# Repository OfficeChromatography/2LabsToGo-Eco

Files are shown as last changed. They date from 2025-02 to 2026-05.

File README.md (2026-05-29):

# 2LabsToGo-Eco

# Important Preliminary Note
<b>In our publication (reference 1) we recommended asking our electronic workshop for a quote on the electronic boards. Unfortunately, that turned out to be very difficult. We therefore recommend contacting Chromnil (https://chromnil.com/), a young start-up also providing the electronic boards or even the 2LabsToGo-Eco ready mounted.<br>
<br>

## 2LabsToGo-Eco combines an analytical (high-performance thin-layer chromatography) and a biological (bioassays) laboratory.

### References:  
<ol>
<li>M.C.O. Romero, K. Jakob, J. Schmidt, T. Nimmerfroh, W. Schwack, G.E.
 Morlock, Consolidating two laboratories into the most sustainable lab of the future: 2LabsToGo-Eco,  Analytica Chimica Acta (2025) 1367, 344103 (https://doi.org/10.1016/j.aca.2025.344103).</li>
<li>A. Haase, W. Schwack, G. Morlock, Humidity control for the 2LabsToGo-Eco, 
Analytica Chimica Acta (2026) 1382, 344811 (https://doi.org/10.1016/j.aca.2025.344811).</li>
<li>W. Schwack, J. Morlock, L. Sing, G. Morlock, Faster Operation of 2LabsToGo-Eco 
 Using Debian 13, Django 5, and Raspberry Pi 5, verified via screening of cannabidiol-containing oils,
 Journal of Planar Chromatography (2026) 39:119–124, (https://doi.org/10.1007/s00764-026-00406-x).</(li>
</ol>
This repository contains the folders for the hardware, firmware, and software for 2LabsToGo-Eco.
For details and instructions consult the given references.

### 1. Raspberry Pi operating system (OS)
The recent Raspberry Pi OS is based on Debain 13 (Trixie, https://www.raspberrypi.com/software/operating-systems/) 
that can be used to install 2LabsToGo-Eco on both the Raspberry Pi 4B and 
the Raspberry Pi 5B (see reference 3).

### 2. Clone the 2LabsToGo-Eco repository
The simplest way to clone a git repository (internet access required!) is opening a new terminal being in the home directory.<br>
Then, copy and paste the next command and press enter.
```bash
git clone https://github.com/OfficeChromatography/2LabsToGo-Eco.git
```
### 3. Installing the software
To install the software, consult this [README](https://github.com/OfficeChromatography/2LabsToGo-Eco/blob/main/2LabsToGo-Eco-Software/README.md).

### 4. Flashing the firmware
Instructions to flash the firmware, can be found [here](https://github.com/OfficeChromatography/2LabsToGo-Eco/blob/main/2LabsToGo-Eco-Firmware/README.md).

### 5. Updating 2LabsToGo-Eco
Instructions to update the 2LabsToGo-Eco folder, consult [this instruction folder](https://github.com/OfficeChromatography/2LabsToGo-Eco/tree/main/2LabsToGo-Update-History).

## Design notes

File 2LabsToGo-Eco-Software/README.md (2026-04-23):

# 2LabsToGo-Eco-Software
## Installation
The installation process is really simple. 

2LabsToGo-Eco-Software works fine on a Raspberry Pi 4B or 5B with 4GB RAM memory.

As operation system, Raspberry Pi OS (Debian 13, trixie, 64-bit) is recommended,
installed by the [Raspberry Pi Imager](https://www.raspberrypi.com/software/) (see reference 3 in 
this [README](https://github.com/OfficeChromatography/2LabsToGo-Eco/blob/main/README.md)).

Before the next steps, consult the [checklist](https://github.com/OfficeChromatography/2LabsToGo-Eco/blob/main/2LabsToGo-Update-History/checklist.pdf) and  [Update Assembly Instruction](https://github.com/OfficeChromatography/2LabsToGo-Eco/blob/main/2LabsToGo-Update-History/UpdateAssemblyInstruction.pdf).

To clone the 2LabsToGo-Eco repository, consult this [README](https://github.com/OfficeChromatography/2LabsToGo-Eco/blob/main/README.md).

### Execute 'install.py'
To install 2LabsToGo-Eco-Software, go to the folder that contains the 2LabsToGo-Eco-Software with

```bash
cd /path/to/your/2LabsToGo-Eco-Software
```
Then execute
```bash
sudo python3 install.py |& tee install-py.log
```

This will install:
```
docker and some software packages
```
After some minutes, 2LabsToGo-Eco-Software is installed in your device.

To start the server execute the run.py file with
```
sudo python3 run.py |& tee run-py.log
```
This process takes a while, when executed the first time. The log files can be consulted in case of any problem.<a>

To quit the Django server, press
```
Ctrl+c 
```

2LabsToGo-Eco-Software was intensively tested with both Chromium and Firefox as browser.

To use the software consult the 2LabsToGo-Eco-Software Manual (see reference 1 in 
this [README](https://github.com/OfficeChromatography/2LabsToGo-Eco/blob/main/README.md)).

### Useful guides

[Docker Commands](https://towardsdatascience.com/15-docker-commands-you-should-know-970ea5203421)

[Remove Migrations](https://simpleisbetterthancomplex.com/tutorial/2016/07/26/how-to-reset-migrations.html)

All commands must be executed inside the docker-compose. To enter to the docker-compose running instance:

In a running container:
```sh
sudo docker-compose exec -ti app bash
```
To initialize and enter the terminal
```sh
sudo docker-compose run -ti app bash
```

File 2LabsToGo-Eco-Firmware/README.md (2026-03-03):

# 2LabsToGo-Eco Firmware 
A Marlin 2.0 3D Printer based Firmware

## Marlin 2.0

Marlin 2.0 takes this popular RepRap firmware to the next level by adding support for much faster 32-bit and ARM-based boards while improving support for 8-bit AVR boards. Read about Marlin's decision to use a "Hardware Abstraction Layer" below.

## Building 2LabsToGo-Eco Firmware

To build the firmware, [PlatformIO](http://docs.platformio.org/en/latest/ide.html#platformio-ide) is preferred. 
Detailed instructions are also available in [Instruction Visual Studio Code](https://github.com/OfficeChromatography/2LabsToGo-Eco/blob/main/2LabsToGo-Eco-Firmware/Instruction%20Visual%20Studio%20Code.pdf).

For building the firmware open the folder 2LabsToGo-Eco-Marlin in Visual Studio Code.
The built firmware.hex file is then saved in 2LabsToGo-Eco-Firmware/2LabsToGo-Eco-Marlin/.pio/build/mega2560.

<b>However, building the firmware is only required, if the Marlin codes have been modified.</b><a>

A pre-built firmware file (firmware_2LabsToGo-Eco.hex) is available in this folder, including files for setting the fuses and flashing the bootloader.
To flash the firmware from the Raspberry Pi onto the Arduino chip of the 2LabsToGo-Eco mainboard, 
use the bash script <u>2LabsToGo-Eco-Firmware/Bullseye/flash_firmware_bullseye.sh</u> or 
<u>2LabsToGo-Eco-Firmware/Trixie/flash_firmware_trixie.sh</u>, depending upon the used Raspberry Pi OS.

For more details on flashing, consult the [2LabsToGo-Eco Assembly guide](https://doi.org/10.1016/j.aca.2025.344103) and reference 3 in this [README](https://github.com/OfficeChromatography/2LabsToGo-Eco/blob/main/README.md).
 
## After firmware update
After a firmware update, both PID tunings must be performed again to save the settings in the firmware.<br>
Consult the [2LabsToGo-Eco Assembly guide](https://doi.org/10.1016/j.aca.2025.344103).

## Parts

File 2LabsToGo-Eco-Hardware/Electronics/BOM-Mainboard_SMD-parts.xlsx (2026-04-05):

 | SMD parts
ID | Designator | Qty. | Manufacturer | Manufacturer Part # | Description | Type | Footprint
1 | C2,C3,C6,C15,C37,C38,C39,C54,C63,C64,C65,C66,C67 | 13 | Panasonic | EEE-FK1E101XP | Aluminium Electrolytic Capacitors - SMD 100uF 25V | SMD | PANASONIC_D_334
2 | C9,C11,C12,C13,C14,C16,C17,C18,C19,C23,C24,C25,C26,C29,C31,C32,C35,C36,C4,C41,C42,C43,C44,C45,C47,C49,C53,C55,C56,C60,C61,C62,C68 | 33 | KEMET | C0805C104K5RACTU | Multilayer Ceramic Capacitors MLCC - SMD/SMT 50V 0.1uF X7R 0805 10% | SMD | C0805
3 | C20,C21 | 2 | KEMET | C0805C220K5RACTU | Multilayer Ceramic Capacitors MLCC - SMD/SMT 50V 22pF X7R 0805 10% | SMD | C0805_334
4 | C28,C33 | 2 | KEMET | C0805C681K5RACTU | Multilayer Ceramic Capacitors MLCC - SMD/SMT 50V 680pF X7R 0805 10% | SMD | C0805_334
5 | C30,C46 | 2 | KEMET | C0805C223K5RACTU | Multilayer Ceramic Capacitors MLCC - SMD/SMT 50V 0.022uF X7R 0805 10% | SMD | C0805_334
6 | C1,C5,C7,C8,C10,C27,C34,C51 | 8 | Panasonic | EEE-FK1E100AR | Aluminium Electrolytic Capacitors - SMD 10UF 25V FK SMD | SMD | PANASONIC_B_334
7 | C22,C48 | 2 | KEMET | C0805C101F3HACTU | Multilayer Ceramic Capacitors MLCC - SMD/SMT 25V 100pF X8R 0805 1% | SMD | C0805_334
8 | C50 | 1 | KEMET | C1812C102KHRACTU | Multilayer Ceramic Capacitors MLCC - SMD/SMT 3kV 1000pF X7R 1812 10% | SMD | C1812_334
9 | C52 | 1 | KEMET | C1812C334KCRACTU | Multilayer Ceramic Capacitors MLCC - SMD/SMT 500V 0.33uF X7R 1812 10% | SMD | C1812_334
10 | C59 | 1 | KEMET | C0805C473K5RACTU | Multilayer Ceramic Capacitors MLCC - SMD/SMT 50V 0.047uF X7R 0805 10% | SMD | C0805
11 | D4,D6,D12,D13,D14,D15 | 6 | onsemi | RGF1G | Rectifiers 400V 1a Rectifier Glass Passivated | SMD | DO214AC_210
12 | D7,D16 | 2 | onsemi | 1N4148WS | Small Signal Switching Diodes Small Signal Diode | SMD | SOD-323_11396254
13 | D1,D2,D10 | 3 | Comchip Technology | SS54-HF | Schottky Diodes & Rectifiers DIODE SCHOTTKY 5A 40V SMA | SMD | DO214AC
14 | D8,D9 | 2 | Vishay | SML4757A-E3/61 | Zener Diodes 51 Volt 1.0W 5% | SMD | DO-214AC-2
15 | IC10 | 1 | Microchip Technology | MIC4420ZM-TR | Gate Drivers 8 SOIC 3.90mm(.150in) T/R | SMD | SOIC-8
16 | IC11,IC12 | 2 | onsemi | LM1117MPX-ADJNOPB | LDO Voltage Regulators LM ANA SOT223 800MA LDO | SMD | SOT-223-3
17 | IC2,IC7 | 2 | Nexperia | 74HC4053D,653 | Multiplexer Switch ICs Triple 2-channel analog multiplexer/demultiplexer | SMD | SOIC-16
18 | IC1,IC4 | 2 | Texas Instruments | NE555DR | Timers & Support Products Precision A 595-NE555D | SMD | SOIC-8
19 | IC3,IC5,IC6 | 3 | Texas Instruments | LM358MX/NOPB | Operational Amplifiers - Op Amps LOW PWR DUAL OP AMP A 926-LM358M/NOPB | SMD | SOIC-8
20 | IC8 | 1 | Texas Instruments | SE555DRG4 | Timers & Support Products Prec Timer ALT 595-SE555DR | SMD | SOIC-8
21 | IC9 | 1 | Diodes Incorporated | AS7805ADTR-G1 | Linear Voltage Regulators 1A 3-Term POS Reg Output 1A | SMD | TO-252-2
22 | Q1,Q2,Q3,Q6,Q7,Q8,Q9 | 7 | Infineon Technologies | IRFR3410TRPBF | MOSFETs 100V SINGLE N-CH 39mOhms 37nC | SMD | TO-252-3
23 | Q5 | 1 | Infineon Technologies | IPD60R180P7SAUMA1 | MOSFETs CONSUMER | SMD | TO-252-3
24 | R10,R9,R56,R55,R6,R2,R26,R5,R8,R54,R100,R4,R82 | 13 | YAGEO | RC0805FR-07100KL | Thick Film Resistors - SMD 100 kOhms 125 mW 0805 1% | SMD | R0805_334
25 | R103,R12 | 2 | YAGEO | RC0805FR-13120RL | Thick Film Resistors - SMD 120Ohms 1/8W 0805 1% | SMD | R0805_334
26 | R13,R14,R15,R31,R47,R53,R87,R99,R106 | 9 | YAGEO | RC0805FR-0710RL | Thick Film Resistors - SMD 10 Ohms 125 mW 0805 1% | SMD | R0805_334
27 | R23,R24,R25,R35,R38,R40,R57,R61,R63,R68,R71,R73,R90,R95,R96,R97 | 16 | YAGEO | RC0805FR-071KL | Thick Film Resistors - SMD 1 kOhms 125 mW 0805 1% | SMD | R0805_334
28 | R16,R18,R19,R20,R27,R29,R32,R36,R43,R45,R48,R58,R65,R69,R76,R78,R79 | 17 | YAGEO | RC0805FR-0710KL | Thick Film Resistors - SMD 10 kOhms 125 mW 0805 1% | SMD | R0805_334
29 | R3,R39,R62,R72 | 4 | YAGEO | RC0805FR-071ML | Thick Film Resistors - SMD 1 MOhms 125 mW 0805 1% | SMD | R0805_334
30 | R66,R67,R77 | 3 | YAGEO | RL1206FR-070R1L | Current Sense Resistors - SMD 100 mOhms 250mW 1 % 600 ppm/C | SMD | R1206_334
31 | R1,R7,R11,R21,R22,R33,R37,R49,R59,R70,R102 | 11 | YAGEO | RC0805FR-074K7L | Thick Film Resistors - SMD 4.7 kOhms 125 mW 0805 1% | SMD | R0805_334
32 | R83 | 1 | YAGEO | RC0805FR-07100RL | Thick Film Resistors - SMD 100 Ohms 125 mW 0805 1% | SMD | R0805_334
33 | R84 | 1 | YAGEO | RC0805JR-7W15KL | Thick Film Resistors - SMD 15kOhms 1/8W 0805 5% | SMD | R0805_334
34 | R89 | 1 | YAGEO | RC0805FR-073KL | Thick Film Resistors - SMD 3 kOhms 125 mW 0805 1% | SMD | R0805_334
35 | R91 | 1 | YAGEO | RC0805FR-0718K2L | Thick Film Resistors - SMD 18.2 kOhms 125 mW 0805 1% | SMD | R0805_334
36 | R94,R92,R30,R98,R28,R46,R101,R93,R44 | 9 | YAGEO | RC0805FR-07330RL | Thick Film Resistors - SMD 330 Ohms 125 mW 0805 1% | SMD | R0805_334
37 | T3,T1,T2,T4 | 4 | Nexperia | BC847C,215 | Bipolar Transistors - BJT 45 V, 100 mA NPN general-purpose transistors | SMD | SOT23_3
38 | T5,T6 | 2 | onsemi | MJD128T4G | Darlington Transistors BIP PNP 8A 120V TR | SMD | TO-252-3
39 | T7,T8,T9 | 3 | onsemi | MJD200G | Bipolar Transistors - BJT 5A 25V 12.5W NPN | SMD | TO-252-3
40 | U$2 | 1 | Texas Instruments | LM2577SX-ADJ/NOPB | IC REG BST FLYBACK ADJ 3A TO263 | SMD | TO-263-5
41 | U2 | 1 | Microchip Technology | ATMEGA2560-16AU | AVR AVR® ATmega Mikrocontroller IC 8-Bit 16MHz 256KB (128K x 16) FLASH 100-TQFP (14x14) | SMD | TQFP-100
42 | U4 | 1 | Texas Instruments | TXB0108PWR | Translation - Voltage Levels 8-Bit Bi-directional V-Level Translator A 595-TXB0108PWRG4 | SMD | TSSOP-20
43 | L1 | 1 | Würth Elektronik | 74477020 | FIXED IND 100UH 2.2A 220 MOHM | SMD
44 | L2 | 1 | Würth Elektronik | 744770222 | FIXED IND 220UH 1.3A 390 MOHM | SMD

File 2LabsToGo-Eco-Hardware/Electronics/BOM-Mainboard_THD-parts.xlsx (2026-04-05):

 | Through hole parts (THD)
ID | Designator | Qty. | Manufacturer | Manufacturer Part # | Description | Type | Footprint
1 | C40, C57, C58 | 3 | Panasonic Electronic Components | EEU-FR1V471L | CAP ALUM 470UF 20% 35V RADIAL TH | THD
2 | J4 | 1 | Kycon Inc. | KPJX-4S-S | CONN JACK FMALE 4POS TIN SOLDER | THD
3 | J5 | 2 | Same Sky (Formerly CUI Devices) | PJ-082BH | CONN PWR JACK 2.5X5.5MM SOLDER | THD
4 | J6 | 1 | 3M | Y2540-6002-SH 40P ST HDR 0.112 GF | 3M FOUR-WALL HEADER 2500 SERIES | THD
5 | Q4 | 1 | Abracon LLC | ABL-16.000MHZ-B2 | CRYSTAL 16.0000MHZ 18PF TH | THD
6 | R105 | 1 | Bourns Inc. | 3296W-1-102LF | TRIMMER 1K OHM 0.5W PC PIN TOP | THD
7 | R34, R50 | 2 | Bourns Inc. | 3296W-1-504LF | TRIMMER 500K OHM 0.5W PC PIN TOP | THD
8 | R41, R64, R74 | 3 | Bourns Inc. | 3296W-1-204LF | TRIMMER 200K OHM 0.5W PC PIN TOP | THD
9 | R81 | 1 | Bourns Inc. | 3296W-1-501LF | TRIMMER 500 OHM 0.5W PC PIN TOP | THD
10 | SV1 | 1 | 3M | Y2514-6002-SH 14P ST HDR 0.112 GF | 3M FOUR-WALL HEADER 2500 SERIES | THD
11 | U$1, U$4, U$6, U$7, U$8 | 20 | Amphenol CS (FCI) | 75915-308GLF | CONN RCPT 8POS 0.1 GOLD PCB | THD
12 | X1, X2, X6, X7, X11 | 5 | Phoenix Contact | 1803426 | TERM BLOCK HDR 2POS 3.81MM | THD
13 | X4 | 2 | Phoenix Contact | 1803455 | TERM BLOCK HDR 5POS 3.81MM | THD
14 | X5 | 1 | Phoenix Contact | 1803471 | TERM BLOCK HDR 7POS 3.81MM | THD
15 | X9 | 1 | Amphenol CS (FCI) | 87520-0010BLF | CONN RCPT USB2.0 TYPEA 4POS R/A | THD
16 | I2C_1, I2C_2, I2C_3, Z-MOT1, Z-MOT2, X-MOT, Y-MOT, E0-MOT, Z-STOP1, Z-STOP2, X-, X+, Y-, Y+, Z+, FAN1 | 3 | Amphenol CS (FCI) | 68002-420HLF | CONN HEADER VERT 20POS 2.54MM 1) | THD
17 | JP3 | 1 | Amphenol CS (FCI) | 67996-408HLF | CONN HEADER VERT 8POS 2.54MM | THD
18 | ISP1, JP1, JP2, JP4, JP5, JP6 | 6 | Amphenol CS (FCI) | 67996-406HLF | CONN HEADER VERT 6POS 2.54MM | THD
19 | SV3 | 1 | Amphenol CS (FCI) | 67996-410HLF | CONN HEADER VERT 10POS 2.54MM | THD
20 | SV4 | 1 | Amphenol CS (FCI) | 67996-420HLF | CONN HEADER VERT 20POS 2.54MM | THD
21 | SV5 | 1 | Amphenol CS (FCI) | 67996-412HLF | CONN HEADER VERT 12POS 2.54MM | THD
22 | X8 | 1 | Phoenix Contact | 1876301 | TERM BLOCK HDR 6POS 3.50MM | THD
23 | SW1 | 1 | TE Connectivity ALCOSWITCH Switches | 1825910-6 | SWITCH TACTILE SPST-NO 0.05A 24V | THD
24 | R88 | 1 | Bourns Inc. | 3296W-1-104ALF | TRIMMER 100K OHM 0.5W PC PIN TOP | THD
25 | J2 | 1 | Mean Well USA Inc. | NID65-5 | DC DC CONVERTER 5V 33W | THD
26 | X10 | 1 | Phoenix Contact | 1755752 | TERM BLOCK HDR 4POS 5.08MM | THD
27 | DHT1 | 1 | Molex | 901471104 | CONN RCPT 4POS 0.1 TIN PCB | THD
 | 1) Header to be cut to 2-pin (FAN1), 3-pin (Z-STOP1, Z-STOP2, X-, X+, Y-, Y+, Z+) and 4-pin (I2C_1, I2C_2, I2C_3, Z-MOT1, Z-MOT2, X-MOT, Y-MOT, E0-MOT) parts, respectively

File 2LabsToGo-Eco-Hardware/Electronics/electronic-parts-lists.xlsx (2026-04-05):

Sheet: mainboard
 | SMD parts
ID | Designator | Manufacturer No | Manufacturer | Description | Termination Style | Footprint | Qty.
1 | C2,C3,C6,C15,C37,C38,C39,C54,C63,C64,C65,C66,C67 | EEE-FK1E101XP | Panasonic | Aluminium Electrolytic Capacitors - SMD 100uF 25V | SMD | PANASONIC_D_334 | 13
2 | C9,C11,C12,C13,C14,C16,C17,C18,C19,C23,C24,C25,C26,C29,C31,C32,C35,C36,C4,C41,C42,C43,C44,C45,C47,C49,C53,C55,C56,C60,C61,C62,C68 | C0805C104K5RACTU | KEMET | Multilayer Ceramic Capacitors MLCC - SMD/SMT 50V 0.1uF X7R 0805 10% | SMD | C0805 | 33
3 | C20,C21 | C0805C220K5RACTU | KEMET | Multilayer Ceramic Capacitors MLCC - SMD/SMT 50V 22pF X7R 0805 10% | SMD | C0805_334 | 2
4 | C28,C33 | C0805C681K5RACTU | KEMET | Multilayer Ceramic Capacitors MLCC - SMD/SMT 50V 680pF X7R 0805 10% | SMD | C0805_334 | 2
5 | C30,C46 | C0805C223K5RACTU | KEMET | Multilayer Ceramic Capacitors MLCC - SMD/SMT 50V 0.022uF X7R 0805 10% | SMD | C0805_334 | 2
6 | C1,C5,C7,C8,C10,C27,C34,C51 | EEE-FK1E100AR | Panasonic | Aluminium Electrolytic Capacitors - SMD 10UF 25V FK SMD | SMD | PANASONIC_B_334 | 8
7 | C22,C48 | C0805C101F3HACTU | KEMET | Multilayer Ceramic Capacitors MLCC - SMD/SMT 25V 100pF X8R 0805 1% | SMD | C0805_334 | 2
8 | C50 | C1812C102KHRACTU | KEMET | Multilayer Ceramic Capacitors MLCC - SMD/SMT 3kV 1000pF X7R 1812 10% | SMD | C1812_334 | 1
9 | C52 | C1812C334KCRACTU | KEMET | Multilayer Ceramic Capacitors MLCC - SMD/SMT 500V 0.33uF X7R 1812 10% | SMD | C1812_334 | 1
10 | C59 | C0805C473K5RACTU | KEMET | Multilayer Ceramic Capacitors MLCC - SMD/SMT 50V 0.047uF X7R 0805 10% | SMD | C0805 | 1
11 | D4,D6,D12,D13,D14,D15 | RGF1G | onsemi | Rectifiers 400V 1a Rectifier Glass Passivated | SMD | DO214AC_210 | 6
12 | D7,D16 | 1N4148WS | onsemi | Small Signal Switching Diodes Small Signal Diode | SMD | SOD-323_11396254 | 2
13 | D1,D2,D10 | SS54-HF | Comchip Technology | Schottky Diodes & Rectifiers DIODE SCHOTTKY 5A 40V SMA | SMD | DO214AC | 3
14 | D8,D9 | SML4757A-E3/61 | Vishay | Zener Diodes 51 Volt 1.0W 5% | SMD | DO-214AC-2 | 2
15 | IC10 | MIC4420ZM-TR | Microchip Technology | Gate Drivers 8 SOIC 3.90mm(.150in) T/R | SMD | SOIC-8 | 1
16 | IC11,IC12 | LM1117MPX-ADJNOPB | onsemi | LDO Voltage Regulators LM ANA SOT223 800MA LDO | SMD | SOT-223-3 | 2
17 | IC2,IC7 | 74HC4053D,653 | Nexperia | Multiplexer Switch ICs Triple 2-channel analog multiplexer/demultiplexer | SMD | SOIC-16 | 2
18 | IC1,IC4 | NE555DR | Texas Instruments | Timers & Support Products Precision A 595-NE555D | SMD | SOIC-8 | 2
19 | IC3,IC5,IC6 | LM358MX/NOPB | Texas Instruments | Operational Amplifiers - Op Amps LOW PWR DUAL OP AMP A 926-LM358M/NOPB | SMD | SOIC-8 | 3
20 | IC8 | SE555DRG4 | Texas Instruments | Timers & Support Products Prec Timer ALT 595-SE555DR | SMD | SOIC-8 | 1
21 | IC9 | AS7805ADTR-G1 | Diodes Incorporated | Linear Voltage Regulators 1A 3-Term POS Reg Output 1A | SMD | TO-252-2 | 1
22 | Q1,Q2,Q3,Q6,Q7,Q8,Q9 | IRFR3410TRPBF | Infineon Technologies | MOSFETs 100V SINGLE N-CH 39mOhms 37nC | SMD | TO-252-3 | 7
23 | Q5 | IPD60R180P7SAUMA1 | Infineon Technologies | MOSFETs CONSUMER | SMD | TO-252-3 | 1
24 | R10,R9,R56,R55,R6,R2,R26,R5,R8,R54,R100,R4,R82 | RC0805FR-07100KL | YAGEO | Thick Film Resistors - SMD 100 kOhms 125 mW 0805 1% | SMD | R0805_334 | 13
25 | R103,R12 | RC0805FR-13120RL | YAGEO | Thick Film Resistors - SMD 120Ohms 1/8W 0805 1% | SMD | R0805_334 | 2
26 | R13,R14,R15,R31,R47,R53,R87,R99,R106 | RC0805FR-0710RL | YAGEO | Thick Film Resistors - SMD 10 Ohms 125 mW 0805 1% | SMD | R0805_334 | 9
27 | R23,R24,R25,R35,R38,R40,R57,R61,R63,R68,R71,R73,R90,R95,R96,R97 | RC0805FR-071KL | YAGEO | Thick Film Resistors - SMD 1 kOhms 125 mW 0805 1% | SMD | R0805_334 | 16
28 | R16,R18,R19,R20,R27,R29,R32,R36,R43,R45,R48,R58,R65,R69,R76,R78,R79 | RC0805FR-0710KL | YAGEO | Thick Film Resistors - SMD 10 kOhms 125 mW 0805 1% | SMD | R0805_334 | 17
29 | R3,R39,R62,R72 | RC0805FR-071ML | YAGEO | Thick Film Resistors - SMD 1 MOhms 125 mW 0805 1% | SMD | R0805_334 | 4
30 | R66,R67,R77 | RL1206FR-070R1L | YAGEO | Current Sense Resistors - SMD 100 mOhms 250mW 1 % 600 ppm/C | SMD | R1206_334 | 3
31 | R1,R7,R11,R21,R22,R33,R37,R49,R59,R70,R102 | RC0805FR-074K7L | YAGEO | Thick Film Resistors - SMD 4.7 kOhms 125 mW 0805 1% | SMD | R0805_334 | 11
32 | R83 | RC0805FR-07100RL | YAGEO | Thick Film Resistors - SMD 100 Ohms 125 mW 0805 1% | SMD | R0805_334 | 1
33 | R84 | RC0805JR-7W15KL | YAGEO | Thick Film Resistors - SMD 15kOhms 1/8W 0805 5% | SMD | R0805_334 | 1
34 | R89 | RC0805FR-073KL | YAGEO | Thick Film Resistors - SMD 3 kOhms 125 mW 0805 1% | SMD | R0805_334 | 1
35 | R91 | RC0805FR-0718K2L | YAGEO | Thick Film Resistors - SMD 18.2 kOhms 125 mW 0805 1% | SMD | R0805_334 | 1
36 | R94,R92,R30,R98,R28,R46,R101,R93,R44 | RC0805FR-07330RL | YAGEO | Thick Film Resistors - SMD 330 Ohms 125 mW 0805 1% | SMD | R0805_334 | 9
37 | T3,T1,T2,T4 | BC847C,215 | Nexperia | Bipolar Transistors - BJT 45 V, 100 mA NPN general-purpose transistors | SMD | SOT23_3 | 4
38 | T5,T6 | MJD128T4G | onsemi | Darlington Transistors BIP PNP 8A 120V TR | SMD | TO-252-3 | 2
39 | T7,T8,T9 | MJD200G | onsemi | Bipolar Transistors - BJT 5A 25V 12.5W NPN | SMD | TO-252-3 | 3
40 | U$2 | LM2577SX-ADJ/NOPB | Texas Instruments | Switching Voltage Regulators Step-Up Vtg Reg A 926-LM2577S-ADJ/NOPB | SMD | TO-263-5 | 1
41 | U2 | ATMEGA2560-16AU | Microchip Technology | AVR AVR® ATmega Mikrocontroller IC 8-Bit 16MHz 256KB (128K x 16) FLASH 100-TQFP (14x14) | SMD | TQFP-100 | 1
42 | U4 | TXB0108PWR | Texas Instruments | Translation - Voltage Levels 8-Bit Bi-directional V-Level Translator A 595-TXB0108PWRG4 | SMD | TSSOP-20 | 1
43 | L1 | 74477020 | Wurth Electronic | Power Inductors - SMD WE-PD 100uH 2.2A DCR=220mOhms AEC-Q200 | surface mount | WE-CHSA_1212_14076700 | 1
44 | L2 | 744770222 | Wurth Electronic | Power Inductors - SMD WE-PD 220uH 1.3A DCR=390mOhms AEC-Q200 | surface mount | WE-CHSA_1212_14076700 | 1
 | Through hole parts
ID | Designator | Manufacturer No | Manufacturer | Description | Termination Style | Footprint | Qty.
1 | C40,C58,C57 | EEU-FR1V471L | Panasonic | Aluminium Electrolytic Capacitors - Radial Leaded 35VDC 470uF 8x20mm LS5mm | Through Hole | E5-10,5_334 | 3
2 | J2 | NID65-5 | MEAN WELL | Non-Isolated DC/DC Converters 32.5W 24Vin 5Vout Non-Iso Reg SIP | Through Hole | SIP-11 | 1
3 | J4 | KPJX-4S-S | Kycon | DC Power Connectors 4P JACK SKT SHIELDED SNAP AND LOCK | Through Hole | KYCON_KPJX-4S-S | 1
4 | J5 | PJ-082BH | Same Sky (https://www.mouser.de/manufacturer/same-sky/) | DC Power Connectors 2.5mm x 5.5mm horz | Through Hole | PJ082BH_vf.QJzKeZqrQ1Gobk2092XC6w | 1
5 | J6 | Y2540-6002-SH 40P ST HDR 0.112 GF | 3M | Headers & Wire Housings 3M Four-Wall Header 2500 Series, 40 Pin Straight Header, 0.112 Tail Length, Gold Flash | Through Hole | 2X20_SHROUDED_513 | 1
6 | Q4 | ABL-16.000MHZ-B2 | ABRACON | Crystals Xtal HC-49/US 3.5mm Height 16MHz Tol +/-20ppm Stab +/-50ppm -20°C ~ 70°C 18pF 40 Ohms | Through Hole | QS_367 | 1
7 | R105 | 3296W-1-102LF | Bourns | Trimmer Resistors - Through Hole 3/8" 1Kohms Sealed Vertical Adjust | Through Hole | RTRIM3296W | 1
8 | R34,R50 | 3296W-1-504LF | Bourns | Trimmer Resistors - Through Hole 3/8" 500Kohms Sealed Vertical Adjust | Through Hole | RTRIM3296W | 2
9 | R74,R64,R41 | 3296W-1-204LF | Bourns | Trimmer Resistors - Through Hole 3/8" 200Kohms Sealed Vertical Adjust | Through Hole | RTRIM3296W | 3
10 | R81 | 3296W-1-501LF | Bourns | Trimmer Resistors - Through Hole 3/8IN 500 OHM Sealed Vertical Adjust | Through Hole | RTRIM3296W | 1
11 | R88 | 3296W-1-104ALF | YAGEO | Trimmer Resistors - Through Hole 3/8" 100Kohms Sealed Vertical Adjust | Through Hole | RTRIM3296W | 1
12 | SV1 | Y2514-6002-SH 14P ST HDR 0.112 GF | 3M | Headers & Wire Housings 3M Four-Wall Header 2500 Series, 14 Pin Straight Header, 0.112 Tail Length, Gold Flash | Through Hole | ML14_149 | 1
13 | SW1 | 1825910-6 | TE Connectivity | Tactile Switches FSM4JH=6MM TACT SWITCH, HIGH TEMP | Through Hole | 1825910-6_11396471 | 1
14 | U$4,U$1,U$6,U$8,U$7 | 535541-6 | TE Connectivity | Headers & Wire Housings VERT RECPT 8 POS | Through Hole | A4988BREAKOUT | 5x2
15 | X10 | 1757268 | Phoenix Contact | Pluggable Terminal Blocks 4 Pos 5.08mm pitch Through Hole Header | Through Hole | MCV4 | 1
16 | X11,X2,X7,X1,X6 | 1803426 | Phoenix Contact | Pluggable Terminal Blocks 2 Pos 3.81mm pitch Through Hole Header | Through Hole | MCV2 | 5
17 | X4 | 1803455 | Phoenix Contact | Pluggable Terminal Blocks 5 Pos 3.81mm pitch Through Hole Header | Through Hole | MCV5 | 1
18 | X5 | 1803471 | Phoenix Contact | Pluggable Terminal Blocks 7 Pos 3.81mm pitch Through Hole Header | Through Hole | MCV7 | 1
19 | X8 | 1876301 | Phoenix Contact | Pluggable Terminal Blocks 6 Pos 3.5mm pitch Through Hole Header | Through Hole | MC6 | 1
20 | X9 | 87520-0010BLF | Amphenol FCI | USB Connectors USB S/D RECEPT | Through Hole | PN87520-S_130 | 1
21 | I2C_3,I2C_1,I2C_2 | 68002-420HLF | Amphenol FCI | Headers & Wire Housings 20P SR UNSHRD HRD TIN OVER NI | Through Hole | MA04-1 | 3
22 | FAN1 | see 21 |  |  | Through Hole | Ma02-1
23 | Z-MOT2,Y-MOT0,X-MOT0,E0-MOT0,Z-MOT1 | see 21 |  |  | Through Hole | MA04-1
24 | Z-STOP2,Y-0,X-0,X+0,Z-STOP1,Z+0,Y+0 | see 21 |  |  | Through Hole | MA03-1
25 | JP3 | 67996-408HLF | Amphenol FCI | Headers & Wire Housings 8P DR UNSHRD HRD TIN OVER NI | Through Hole | MA04_2, 2x4 pins | 1
26 | SV3 | 67996-410HLF | Amphenol FCI | Headers & Wire Housings 10P DR UNSHRD HRD TIN OVER NI | Through Hole | MA05-2, 2x5 pins | 1
27 | SV4 | 67996-420HLF | Amphenol FCI | Headers & Wire Housings 20P DR UNSHRD HRD TIN OVER NI | Through Hole | MA10-2, 2x10 pins | 1
28 | SV5 | 67996-412HLF | Amphenol FCI | Headers & Wire Housings 12P DR UNSHRD HRD TIN OVER NI | Through Hole | MA06-2, 2x6 pins | 1
 | DHT1?
 | Extern buttom??

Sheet: mainboard-smd
 | SMD parts
ID | Designator | Manufacturer No | Manufacturer | Description | Termination Style | Footprint | Qty.
1 | C2,C3,C6,C15,C37,C38,C39,C54,C63,C64,C65,C66,C67 | EEE-FK1E101XP | Panasonic | Aluminium Electrolytic Capacitors - SMD 100uF 25V | SMD | PANASONIC_D_334 | 13
2 | C9,C11,C12,C13,C14,C16,C17,C18,C19,C23,C24,C25,C26,C29,C31,C32,C35,C36,C4,C41,C42,C43,C44,C45,C47,C49,C53,C55,C56,C60,C61,C62,C68 | C0805C104K5RACTU | KEMET | Multilayer Ceramic Capacitors MLCC - SMD/SMT 50V 0.1uF X7R 0805 10% | SMD | C0805 | 33
3 | C20,C21 | C0805C220K5RACTU | KEMET | Multilayer Ceramic Capacitors MLCC - SMD/SMT 50V 22pF X7R 0805 10% | SMD | C0805_334 | 2
4 | C28,C33 | C0805C681K5RACTU | KEMET | Multilayer Ceramic Capacitors MLCC - SMD/SMT 50V 680pF X7R 0805 10% | SMD | C0805_334 | 2
5 | C30,C46 | C0805C223K5RACTU | KEMET | Multilayer Ceramic Capacitors MLCC - SMD/SMT 50V 0.022uF X7R 0805 10% | SMD | C0805_334 | 2
6 | C1,C5,C7,C8,C10,C27,C34,C51 | EEE-FK1E100AR | Panasonic | Aluminium Electrolytic Capacitors - SMD 10UF 25V FK SMD | SMD | PANASONIC_B_334 | 8
7 | C22,C48 | C0805C101F3HACTU | KEMET | Multilayer Ceramic Capacitors MLCC - SMD/SMT 25V 100pF X8R 0805 1% | SMD | C0805_334 | 2
8 | C50 | C1812C102KHRACTU | KEMET | Multilayer Ceramic Capacitors MLCC - SMD/SMT 3kV 1000pF X7R 1812 10% | SMD | C1812_334 | 1
9 | C52 | C1812C334KCRACTU | KEMET | Multilayer Ceramic Capacitors MLCC - SMD/SMT 500V 0.33uF X7R 1812 10% | SMD | C1812_334 | 1
10 | C59 | C0805C473K5RACTU | KEMET | Multilayer Ceramic Capacitors MLCC - SMD/SMT 50V 0.047uF X7R 0805 10% | SMD | C0805 | 1
11 | D4,D6,D12,D13,D14,D15 | RGF1G | onsemi | Rectifiers 400V 1a Rectifier Glass Passivated | SMD | DO214AC_210 | 6
12 | D7,D16 | 1N4148WS | onsemi | Small Signal Switching Diodes Small Signal Diode | SMD | SOD-323_11396254 | 2
13 | D1,D2,D10 | SS54-HF | Comchip Technology | Schottky Diodes & Rectifiers DIODE SCHOTTKY 5A 40V SMA | SMD | DO214AC | 3
14 | D8,D9 | SML4757A-E3/61 | Vishay | Zener Diodes 51 Volt 1.0W 5% | SMD | DO-214AC-2 | 2
15 | IC10 | MIC4420ZM-TR | Microchip Technology | Gate Drivers 8 SOIC 3.90mm(.150in) T/R | SMD | SOIC-8 | 1
16 | IC11,IC12 | LM1117MPX-ADJNOPB | onsemi | LDO Voltage Regulators LM ANA SOT223 800MA LDO | SMD | SOT-223-3 | 2
17 | IC2,IC7 | 74HC4053D,653 | Nexperia | Multiplexer Switch ICs Triple 2-channel analog multiplexer/demultiplexer | SMD | SOIC-16 | 2
18 | IC1,IC4 | NE555DR | Texas Instruments | Timers & Support Products Precision A 595-NE555D | SMD | SOIC-8 | 2
19 | IC3,IC5,IC6 | LM358MX/NOPB | Texas Instruments | Operational Amplifiers - Op Amps LOW PWR DUAL OP AMP A 926-LM358M/NOPB | SMD | SOIC-8 | 3
20 | IC8 | SE555DRG4 | Texas Instruments | Timers & Support Products Prec Timer ALT 595-SE555DR | SMD | SOIC-8 | 1
21 | IC9 | AS7805ADTR-G1 | Diodes Incorporated | Linear Voltage Regulators 1A 3-Term POS Reg Output 1A | SMD | TO-252-2 | 1
22 | Q1,Q2,Q3,Q6,Q7,Q8,Q9 | IRFR3410TRPBF | Infineon Technologies | MOSFETs 100V SINGLE N-CH 39mOhms 37nC | SMD | TO-252-3 | 7
23 | Q5 | IPD60R180P7SAUMA1 | Infineon Technologies | MOSFETs CONSUMER | SMD | TO-252-3 | 1
24 | R10,R9,R56,R55,R6,R2,R26,R5,R8,R54,R100,R4,R82 | RC0805FR-07100KL | YAGEO | Thick Film Resistors - SMD 100 kOhms 125 mW 0805 1% | SMD | R0805_334 | 13
25 | R103,R12 | RC0805FR-13120RL | YAGEO | Thick Film Resistors - SMD 120Ohms 1/8W 0805 1% | SMD | R0805_334 | 2
26 | R13,R14,R15,R31,R47,R53,R87,R99,R106 | RC0805FR-0710RL | YAGEO | Thick Film Resistors - SMD 10 Ohms 125 mW 0805 1% | SMD | R0805_334 | 9
27 | R23,R24,R25,R35,R38,R40,R57,R61,R63,R68,R71,R73,R90,R95,R96,R97 | RC0805FR-071KL | YAGEO | Thick Film Resistors - SMD 1 kOhms 125 mW 0805 1% | SMD | R0805_334 | 16
28 | R16,R18,R19,R20,R27,R29,R32,R36,R43,R45,R48,R58,R65,R69,R76,R78,R79 | RC0805FR-0710KL | YAGEO | Thick Film Resistors - SMD 10 kOhms 125 mW 0805 1% | SMD | R0805_334 | 17
29 | R3,R39,R62,R72 | RC0805FR-071ML | YAGEO | Thick Film Resistors - SMD 1 MOhms 125 mW 0805 1% | SMD | R0805_334 | 4
30 | R66,R67,R77 | RL1206FR-070R1L | YAGEO | Current Sense Resistors - SMD 100 mOhms 250mW 1 % 600 ppm/C | SMD | R1206_334 | 3
31 | R1,R7,R11,R21,R22,R33,R37,R49,R59,R70,R102 | RC0805FR-074K7L | YAGEO | Thick Film Resistors - SMD 4.7 kOhms 125 mW 0805 1% | SMD | R0805_334 | 11
32 | R83 | RC0805FR-07100RL | YAGEO | Thick Film Resistors - SMD 100 Ohms 125 mW 0805 1% | SMD | R0805_334 | 1
33 | R84 | RC0805JR-7W15KL | YAGEO | Thick Film Resistors - SMD 15kOhms 1/8W 0805 5% | SMD | R0805_334 | 1
34 | R89 | RC0805FR-073KL | YAGEO | Thick Film Resistors - SMD 3 kOhms 125 mW 0805 1% | SMD | R0805_334 | 1
35 | R91 | RC0805FR-0718K2L | YAGEO | Thick Film Resistors - SMD 18.2 kOhms 125 mW 0805 1% | SMD | R0805_334 | 1
36 | R94,R92,R30,R98,R28,R46,R101,R93,R44 | RC0805FR-07330RL | YAGEO | Thick Film Resistors - SMD 330 Ohms 125 mW 0805 1% | SMD | R0805_334 | 9
37 | T3,T1,T2,T4 | BC847C,215 | Nexperia | Bipolar Transistors - BJT 45 V, 100 mA NPN general-purpose transistors | SMD | SOT23_3 | 4
38 | T5,T6 | MJD128T4G | onsemi | Darlington Transistors BIP PNP 8A 120V TR | SMD | TO-252-3 | 2
39 | T7,T8,T9 | MJD200G | onsemi | Bipolar Transistors - BJT 5A 25V 12.5W NPN | SMD | TO-252-3 | 3
40 | U$2 | LM2577SX-ADJ/NOPB | Texas Instruments | Switching Voltage Regulators Step-Up Vtg Reg A 926-LM2577S-ADJ/NOPB | SMD | TO-263-5 | 1
41 | U2 | ATMEGA2560-16AU | Microchip Technology | AVR AVR® ATmega Mikrocontroller IC 8-Bit 16MHz 256KB (128K x 16) FLASH 100-TQFP (14x14) | SMD | TQFP-100 | 1
42 | U4 | TXB0108PWR | Texas Instruments | Translation - Voltage Levels 8-Bit Bi-directional V-Level Translator A 595-TXB0108PWRG4 | SMD | TSSOP-20 | 1
43 | L1 | 74477020 | Wurth Electronic | Power Inductors - SMD WE-PD 100uH 2.2A DCR=220mOhms AEC-Q200 | surface mount | WE-CHSA_1212_14076700 | 1
44 | L2 | 744770222 | Wurth Electronic | Power Inductors - SMD WE-PD 220uH 1.3A DCR=390mOhms AEC-Q200 | surface mount | WE-CHSA_1212_14076700 | 1

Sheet: status led board
ID | Designator | Manufacturer No | Manufacturer | Description | Termination Style | Footprint | Qty.
1 | LED1, LED2, LED3 | APT2012SGC | Kingbright | LED green | SMD | CHIP-LED0805 | 3
2 | LED4, LED5, LED6, LED8, LED9, LED10 | APT2012SURCK | Kingbright | LED red | SMD | CHIP-LED0805 | 6
3 | LED7, LED11 | APT2012SYCK | Kingbright | LED yellow | SMD | CHIP-LED0805 | 3
4 | SV1 | Y2514-6002-SH 14P ST HDR 0.112 GF | 3M |  | Through Hole | ML14_149 | 1

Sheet: UV led boards
UV led board 265 nm
ID | Designator | Manufacturer No | Manufacturer | Seller | Description | Termination Style | Footprint | Qty.
1 | R1206 | ERJ-8BQF4R3V | Panasonic | Mouser, Digikey | Current Sense Resistors - SMD 1206 4.3ohm 1% Curr Sense AEC-Q200 | SMD |  | 4
2 | UV-LED | PKC-H10-F35 | Photon Wave | Lasercomponents | UVC-LED, 265nm +/-5nm, typ. 18mW, SMD3535 | SMD3535 |  | 4
UV led board 365 nm
ID | Designator | Manufacturer No | Manufacturer | Seller | Description | Termination Style | Footprint | Qty.
1 | R1206 | CRM1206-FX-20R0ELF | Bourns | Mouser, Digikey | Current Sense Resistors - SMD CHIP RESISTOR Low Value | SMD |  | 4
2 | UV-LED | IN-C33CTNU2 | Inolux | Digikey | Ultraviolet (UV) Emitter 365nm ~ 370nm 3.5V 1A 120° 1414 (3535 Metric) | SMD3535 |  | 4

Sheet: plugs and cables
Plugs and cables
ID | Designator | Manufacturer No | Manufacturer | Description | Qty.
1 | jumper 2x3, motor driver ports | 69145-206LF | Amphenol FCI | 6 (2 x 3) Position Shunt Connector Black Open Top 0.100" (2.54mm) Gold or Gold, GXT™ | 5
2 | jumper 2x4, ISP to Pi | 69145-108LF | Amphenol FCI | 8 (2 x 4) Position Shunt Connector Black Open Top 0.100" (2.54mm) Gold or Gold, GXT™ | 1
3 | Raspberry Pi GPIO cable | IDSD-20-D-02.00 | Samtec | 40 Position Cable Assembly Rectangular Socket to Socket 0.167' (50.80mm, 2.00") | 1
4 | cable status LED board | IDSS-14-D-05.00 | Samtec | 14 Position Cable Assembly Rectangular Socket to Socket | 1
5 | plug external port | TJ0451560000G | Amphenol Anytek | 4 Position Terminal Block Plug, Female Sockets 0.200" (5.08mm) 180° Free Hanging (In-Line) | 1
6 | plug plate holder power | 1803604 | Phoenix Contact | 5 Position Terminal Block Plug, Female Sockets 0.150" (3.81mm) 180° Free Hanging (In-Line) | 1
7 | plug LED's power | 1803620 | Phoenix Contact | 7 Position Terminal Block Plug, Female Sockets 0.150" (3.81mm) 180° Free Hanging (In-Line) | 1
8 | plug micro pump, 3-way valve, dispensing valve, case light, nebulizer | 1803578 | Phoenix Contact | 2 Position Terminal Block Plug, Female Sockets 0.150" (3.81mm) 180° Free Hanging (In-Line) | 5
9 | plug mini-incubator | 1840405 | Phoenix Contact | 6 Position Terminal Block Plug, Female Sockets 0.138" (3.50mm) 180° Free Hanging (In-Line) | 1

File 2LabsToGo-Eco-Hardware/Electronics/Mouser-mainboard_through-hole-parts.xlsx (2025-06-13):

SHOPPING BASKET
This is not an invoice
02-Jun-25 07:16:33
 | Mouser No | Mfr. No | Manufacturer | Customer No | Description | RoHS | Lifecycle | Order Qty. | Price (EUR) | Ext.: (EUR)
1 | 667-EEU-FR1V471L | EEU-FR1V471L | Panasonic |  | Aluminium Electrolytic Capacitors - Radial Leaded 35VDC 470uF 8x20mm LS5mm | RoHS Compliant |  | 3 | 0,684 € | 2,05 €
2 | 709-NID65-5 | NID65-5 | MEAN WELL |  | Non-Isolated DC/DC Converters 32.5W 24Vin 5Vout Non-Iso Reg SIP | RoHS Compliant |  | 1 | 12,42 € | 12,42 €
3 | 651-1876301 | 1876301 | Phoenix Contact |  | Pluggable Terminal Blocks 6 Pos 3.5mm pitch Through Hole Header | RoHS Compliant |  | 2 | 2,22 € | 4,44 €
4 | 806-KPJX-4S-S | KPJX-4S-S | Kycon |  | DC Power Connectors 4P JACK SKT SHIELDED SNAP AND LOCK | RoHS Compliant |  | 1 | 2,22 € | 2,22 €
5 | 490-PJ-082BH | PJ-082BH | Same Sky |  | DC Power Connectors 2.5mm x 5.5mm horz | RoHS Compliant |  | 1 | 1,69 € | 1,69 €
6 | 517-2540-600240ST112 | Y2540-6002-SH 40P ST HDR 0.112 GF | 3M |  | Headers & Wire Housings 3M Four-Wall Header 2500 Series, 40 Pin Straight Header, 0.112 Tail Length, Gold Flash | RoHS Compliant | New Product | 1 | 2,31 € | 2,31 €
7 | 710-74477020 | 74477020 | Wurth Elektronik |  | Power Inductors - SMD WE-PD 100uH 2.2A DCR=220mOhms AEC-Q200 | RoHS Compliant |  | 1 | 1,91 € | 1,91 €
8 | 710-744770222 | 744770222 | Wurth Elektronik |  | Power Inductors - SMD WE-PD 220uH 1.3A DCR=390mOhms AEC-Q200 | RoHS Compliant |  | 2 | 2,20 € | 4,40 €
9 | 815-ABL-16-B2 | ABL-16.000MHZ-B2 | ABRACON |  | Crystals Xtal HC-49/US 3.5mm Height 16MHz Tol +/-20ppm Stab +/-50ppm -20°C ~ 70°C 18pF 40 Ohms | RoHS Compliant |  | 1 | 0,304 € | 0,30 €
10 | 652-3296W-1-102LF | 3296W-1-102LF | Bourns |  | Trimmer Resistors - Through Hole 3/8" 1Kohms Sealed Vertical Adjust | RoHS Compliant By Exemption |  | 1 | 1,95 € | 1,95 €
11 | 652-3296W-1-504LF | 3296W-1-504LF | Bourns |  | Trimmer Resistors - Through Hole 3/8" 500Kohms Sealed Vertical Adjust | RoHS Compliant By Exemption |  | 2 | 1,95 € | 3,90 €
12 | 652-3296W-1-204LF | 3296W-1-204LF | Bourns |  | Trimmer Resistors - Through Hole 3/8" 200Kohms Sealed Vertical Adjust | RoHS Compliant By Exemption |  | 3 | 1,95 € | 5,85 €
13 | 652-3296W-1-501LF | 3296W-1-501LF | Bourns |  | Trimmer Resistors - Through Hole 3/8IN 500 OHM Sealed Vertical Adjust | RoHS Compliant |  | 1 | 1,95 € | 1,95 €
14 | 652-3296W-1-104ALF | 3296W-1-104ALF | Bourns |  | Trimmer Resistors - Through Hole 3/8" 100Kohms Sealed Vertical Adjust | RoHS Compliant By Exemption |  | 1 | 3,11 € | 3,11 €
15 | 517-2514-600214ST112 | Y2514-6002-SH 14P ST HDR 0.112 GF | 3M |  | Headers & Wire Housings 3M Four-Wall Header 2500 Series, 14 Pin Straight Header, 0.112 Tail Length, Gold Flash | RoHS Compliant | New Product | 1 | 1,25 € | 1,25 €
16 | 650-1825910-6 | 1825910-6 | TE Connectivity |  | Tactile Switches FSM4JH=6MM TACT SWITCH, HIGH TEMP | RoHS Compliant By Exemption | New At Mouser | 1 | 0,124 € | 0,12 €
17 | 571-5355416 | 535541-6 | TE Connectivity |  | Headers & Wire Housings VERT RECPT 8 POS | No |  | 10 | 1,42 € | 14,20 €
18 | 651-1757268 | 1757268 | Phoenix Contact |  | Pluggable Terminal Blocks 4 Pos 5.08mm pitch Through Hole Header | RoHS Compliant |  | 1 | 1,20 € | 1,20 €
19 | 651-1803426 | 1803426 | Phoenix Contact |  | Pluggable Terminal Blocks 2 Pos 3.81mm pitch Through Hole Header | RoHS Compliant |  | 5 | 0,713 € | 3,57 €
20 | 651-1803455 | 1803455 | Phoenix Contact |  | Pluggable Terminal Blocks 5 Pos 3.81mm pitch Through Hole Header | RoHS Compliant |  | 1 | 1,91 € | 1,91 €
21 | 651-1803471 | 1803471 | Phoenix Contact |  | Pluggable Terminal Blocks 7 Pos 3.81mm pitch Through Hole Header | RoHS Compliant |  | 1 | 2,57 € | 2,57 €
22 | 649-87520-0010BLF | 87520-0010BLF | Amphenol |  | USB Connectors USB S/D RECEPT | RoHS Compliant |  | 1 | 0,941 € | 0,94 €
23 | 649-68002-420HLF | 68002-420HLF | Amphenol |  | Headers & Wire Housings 20P SR UNSHRD HRD TIN OVER NI | RoHS Compliant |  | 3 | 0,922 € | 2,77 €
24 | 649-67996-408HLF | 67996-408HLF | Amphenol |  | Headers & Wire Housings 8P DR UNSHRD HRD TIN OVER NI | RoHS Compliant |  | 1 | 0,295 € | 0,30 €
25 | 649-67996-410HLF | 67996-410HLF | Amphenol |  | Headers & Wire Housings 10P DR UNSHRD HRD TIN OVER NI | RoHS Compliant |  | 1 | 1,25 € | 1,25 €
26 | 649-67996-420HLF | 67996-420HLF | Amphenol |  | Headers & Wire Housings 20P DR UNSHRD HRD TIN OVER NI | RoHS Compliant |  | 1 | 0,675 € | 0,68 €
27 | 649-67996-412HLF | 67996-412HLF | Amphenol |  | Headers & Wire Housings 12P DR UNSHRD HRD TIN OVER NI | RoHS Compliant |  | 1 | 0,295 € | 0,30 €
By submitting your order you agree to these terms and conditions. (https://www.mouser.de/saleterms) |  |  |  |  |  |  |  |  | Merchandise: | 79,56 €
Prices are reflected at the date and time shown. |  |  |  |  |  |  |  |  | Delivery Charge: | 0,00 €
 |  |  |  |  |  |  |  |  | Back-order Delivery: | 0,00 €

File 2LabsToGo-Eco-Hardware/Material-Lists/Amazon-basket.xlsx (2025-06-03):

Amazon products
 | Amazon Product No. | Quantity | Unit price | Net
Nema16 Linear Stepper Motor 16HSL3404 12 V 0.01 Step 100 mm |  | 2 | 14.44 | 28.88
https://www.amazon.de/gp/product/B072JGWTG6/ref=ppx_yo_dt_b_asin_title_o01_s00?ie=UTF8&psc=1 | B072JGWTG6
UPERFECT Portable Monitor, 15.6 Inch Portable Monitor Display 1920 x 1080P Full HD |  | 1 | 126.04 | 126.04
https://www.amazon.de/gp/product/B09P143FD6/ref=ppx_yo_dt_b_asin_title_o02_s03?ie=UTF8&psc=1 | B09P143FD6
Logitech MK220 Wireless Keyboard and Mouse set |  | 1 | 21.46 | 21.46
https://www.amazon.de/gp/product/B006YYNGNY/ref=ppx_yo_dt_b_asin_title_o01_s00?ie=UTF8&psc=1 | B006YYNGNY
SBS® Neodymium Magnets, Pack of 20, Super Magnets with Extreme Hold Disc Magnet 8 x 3 mm |  | 1 | 4.95 | 4.95
https://www.amazon.de/gp/product/B0187JGP1I/ref=ppx_yo_dt_b_asin_title_o02_s02?ie=UTF8&psc=1 | B0187JGP1I
15 x cube magnets, neodymium magnet in 5 mm x 5 mm |  | 1 | 3.78 | 3.78
https://www.amazon.de/gp/product/B005PKWZVW/ref=ppx_yo_dt_b_asin_title_o00_s00?ie=UTF8&psc=1 | B005PKWZVW
3D Printer Mechanical Limit Switch, MakerBot 4 pins, pack of 6, with cables |  | 1 | 5.56 | 5.56
https://www.amazon.de/gp/product/B097436BBZ/ref=ppx_yo_dt_b_asin_title_o02_s01?ie=UTF8&psc=1 | B097436BBZ
3D Printer Optical Limit Switch, pack of 5, with cables |  | 1 | 5.64 | 5.64
https://www.amazon.de/gp/product/B07CQWPLWB/ref=ppx_yo_dt_b_asin_title_o02_s02?ie=UTF8&psc=1 | B07CQWPLWB
60mm bubble spirit level |  | 1 | 7.13 | 7.13
https://www.amazon.de/gp/product/B08882Y16G/ref=ox_sc_act_title_1?smid=A21312XZUBAZON&psc=1 | B08882Y16G
3M 9088 Double-Sided Tape, 6 mm |  | 1 | 5.63 | 5.63
https://www.amazon.de/-/en/Double-Sided-Extra-Sticky-Polyethylene-Terephthalate-Available/dp/B00G6SCZ9Y/ | B00G6SCZ9Y
 |  |  | total | 209.07
 |  |  | incl. VAT | 248.80

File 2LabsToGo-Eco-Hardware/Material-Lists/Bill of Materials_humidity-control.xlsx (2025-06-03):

Parts | Amount | Exemplary seller | Euro (+VAT)
Fan MECHATRONICS MD4028V12B-RSR, 12VDC, 40mm L x 40mm H, 24.3cfm (0.680m³/min) (Digikey No. 1570-1126-ND) | 1 | Digikey | 11.31
Jumper Wire Male to Female 12.00" (304.80mm) 26 AWG, pack of 10, diff. colors (Digikey No. 2183-4567-ND) | 1 | Digikey | 2.81
Plexiglas 215 mm x 190 mm x 3 mm (front_215x190.dxf) | 1 | kunstoffplattenonline.de | 5.00
Round magnets, Ø 8 mm x 3 mm | 10 | supermagnete.de | 4.45
Superglue | 1 | local workshop | 4.90
Screw M3x40 | 4 | local workshop | 0.80
Nut M3 | 4 | local workshop | 0.60
Double-Sided Adhesive Tape tape, 6 mm, 50 cm needed | 1 | local workshop | 6.50
Eurostyle terminal strip with screws, 0.5 - 1.5 mm2 | 1 | local workshop | 2.00
 |  |  | 38.37

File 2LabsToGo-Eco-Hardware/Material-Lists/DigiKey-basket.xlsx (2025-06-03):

Quantity | DigiKey Part number | Manufacturer | Manufacturer part number | Short description | Unit price | Amount | Total price EUR
2 | 495-2143-ND | EPCOS - TDK Electronics | B57861S0104F040V24 | THERM NTC 100KOHM 4540K BEAD | 2.61 | 2 | 5.22 | mini-incubator
16 | 1647-12V-MB-CW-12MCT-ND | Inspired LED, LLC | 12V-MB-CW-12M | LED ENG CW 3LEDS 6000K 12M REEL | 0.33 | 16 | 5.28 | 8 for backlight, 8 for caselight
1 | 223-FX29K0-100A-0010-L-ND | TE Connectivity Measurement Specialties | FX29K0-100A-0010-L | 10LBF COMPRESSION LOAD CELL, I2C | 40.42 | 1 | 40.42
4 | 1830-1187-1-ND | Inolux | IN-C33CTNU2 | TOP VIEW 3535 3.5X3.5X2.0 | 6.36 | 4 | 25.44
2 | 1528-1595-ND | Adafruit Industries LLC | 2869 | ADDRESS LED MODULE SERIAL RGBW | 7.52 | 2 | 15.04
3 | 2786-B21/16BLACKSPL-DS-ND | Sumitomo Electric Interconnect Products, Inc. | B2 1/16 BLACK SPL | SUMITUBE B2 - HEAT-SHRINK FEET | 0.81 | 3 | 2.43
2 | 839-10-04495-ND | Tensility International Corp | 10-04495 | CABLE MALE TO WIRE LEAD 5P 1.64', plug | 10.05 | 2 | 20.10
1 | WM21514-ND | Molex | 1200848027 | CBL CIRC 5POS FEM TO WIRE 1.64', socket | 5.98 | 1 | 5.98
1 | T1422-1-ND | Tensility International Corp | 30-01304 | CABLE 7COND 22AWG BLACK 1M | 4.71 | 1 | 4.71 |  | mini-incubator
1 | WM7736-ND | Molex | 395000006 | TERM BLOCK PLUG 6POS STR 3.5MM | 2.39 | 1 | 2.39 | x | mini-incubator
5 | WM7732-ND | Molex | 395000002 | TERM BLOCK PLUG 2POS STR 3.5MM | 1.09 | 5 | 5.45 | x
1 | WM7735-ND | Molex | 395000005 | TERM BLOCK PLUG 5POS STR 3.5MM | 2.01 | 1 | 2.01 | x
1 | WM7737-ND | Molex | 395000007 | TERM BLOCK PLUG 7POS STR 3.5MM | 2.79 | 1 | 2.79 | x
1 | WM7953-ND | Molex | 395300004 | TERM BLOCK PLUG 4POS STR 5.08MM | 2.93 | 1 | 2.93 | x
1 | 1528-2617-ND | Adafruit Industries LLC | 3814 | JST PH 2 PIN CABLE MALE HEADER 2 | 0.69 | 1 | 0.69 | nebulizer
1 | 455-2267-ND | JST Sales America Inc. | XHP-4 | CONN RCPT HSG 4POS 2.50MM | 0.1 | 1 | 0.10 |  | mini-incubator
3 | 455-1135-1-ND | JST Sales America Inc. | SXH-001T-P0.6 | CONN SOCKET 22-28AWG CRIMP TIN | 0.09 | 3 | 0.27 |  | mini-incubator
1 | 732-13706-ND | Würth Elektronik | 97791003111 | PAN HEAD SCREW_M3 X 10MM CROSS S | 0.25 | 1 | 0.25
1 | 993-1038-ND | PHIHONG USA CORPORATION | AC30UEU | CORD CEE 7/7 TO IEC 320-C13 6' | 5.49 | 1 | 5.49
5 | 732-13622-ND | Würth Elektronik | 60910313421 | WR-PHD_2.54MM_JUMPER_BLACK W/ TE | 0.43 | 5 | 2.15 | x
1 | 732-13623-ND | Würth Elektronik | 60910413421 | WR-PHD_2.54MM_JUMPER_BLACK W/ TE | 0.43 | 1 | 0.43 | x
4 | 732-5317-ND | Würth Elektronik | 61300411121 | CONN HEADER VERT 4POS 2.54MM | 0.17 | 4 | 0.68
1 | IDSD-20-D-02.00-T-ND | Samtec Inc. | IDSD-20-D-02.00-T | INSULATION DISPLACEMENT TERMINAL | 14.94 | 1 | 14.94 | x | Raspberry Pi GPIO
1 | IDSD-07-D-05.00-G-ND | Samtec Inc. | IDSD-07-D-05.00-G | INSULATION DISPLACEMENT TERMINAL | 9.91 | 1 | 9.91 | x | Status LED board
1 | SQP20AJB-10R-ND | YAGEO | SQP20AJB-10R | RES 10 OHM 5% 20W AXIAL | 1.16 | 1 | 1.16
 |  |  |  |  | total |  | 176.26
 |  |  |  |  | incl. VAT |  | 209.75
 | x | included, if the mainboard was ordered from the Electronics workshop, JLU Giessen

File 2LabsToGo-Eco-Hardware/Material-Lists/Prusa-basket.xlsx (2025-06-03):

Prusa basket
Amount | Part description | Unit price | Total price EUR
1 | Stepper motor Z-axis Right (MK3/S/+, MK2.5/S, MK2/S) | 32.68 | 32.68
1 | Hotend PTFE tube (MK2.5S, MK3S, MMU2S) | 1.08 | 1.08
2 | Timing pulley T16-2GT | 2.59 | 5.18
1 | Timing belt 2GT X-axis, MK3 | 4.87 | 4.87
1 | Timing belt 2GT X-axis, MINI | 3.35 | 3.35
1 | Trapezoid nut (i3, MK4, MMU2/2S/3) | 5.86 | 5.86
 |  | total | 53.02
 |  | incl. VAT | 63.09

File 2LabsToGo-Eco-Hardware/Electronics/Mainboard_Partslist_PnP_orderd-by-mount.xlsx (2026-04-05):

Part | Value | Package | Library | Position mm |  | Orientation
Surface-mounted devices
C1 | 10u | PANASONIC_B | rcl | 92.71 | 107.95 | R180
C2 | 100u | PANASONIC_D | rcl | 140.335 | 50.8 | R90
C3 | 100u | PANASONIC_D | rcl | 99.3775 | 5.106 | R90
C4 | 100n | C0805 | rcl | 68.8975 | 63.1825 | R180
C5 | 10u | PANASONIC_B | rcl | 92.71 | 112.395 | R180
C6 | 100u | PANASONIC_D | rcl | 91.44 | 99.06 | R0
C7 | 10u | PANASONIC_B | rcl | 35.56 | 111.76 | R180
C8 | 10u | PANASONIC_B | rcl | 41.91 | 69.85 | R90
C9 | 100n | C0805 | rcl | 135.89 | 49.53 | R270
C10 | 10u | PANASONIC_B | rcl | 88.9 | 123.19 | R0
C11 | 100n | C0805 | rcl | 77.47 | 8.89 | R90
C12 | 100n | C0805 | rcl | 74.93 | 8.89 | R90
C13 | 100n | C0805 | rcl | 82.55 | 8.89 | R90
C14 | 100n | C0805 | rcl | 80.01 | 8.89 | R90
C15 | 100u | PANASONIC_D | rcl | 16.484 | 133.35 | R0
C16 | 100n | C0805 | rcl | 85.09 | 8.89 | R90
C17 | 100n | C0805 | rcl | 73.025 | 42.8625 | R0
C18 | 100n | C0805 | rcl | 85.09 | 63.8175 | R90
C19 | 100n | C0805 | rcl | 65.7225 | 62.5475 | R90
C20 | 22p | C0805 | rcl | 90.805 | 43.18 | R180
C21 | 22p | C0805 | rcl | 90.805 | 38.1 | R180
C22 | 100p | C0805 | rcl | 74.295 | 39.6875 | R90
C23 | 100n | C0805 | rcl | 140.6525 | 38.1 | R0
C24 | 100n | C0805 | rcl | 139.3825 | 45.72 | R0
C25 | 100n | C0805 | rcl | 10.795 | 111.76 | R0
C26 | 100n | C0805 | rcl | 16.1925 | 102.235 | R270
C27 | 10u | PANASONIC_B | rcl | 5.08 | 111.76 | R180
C28 | 680p | C0805 | rcl | 109.5375 | 34.29 | R90
C29 | 100n | C0805 | rcl | 120.3325 | 38.1 | R0
C30 | 22n | C0805 | rcl | 119.0625 | 45.72 | R0
C31 | 100n | C0805 | rcl | 26.035 | 111.76 | R0
C32 | 100n | C0805 | rcl | 31.4325 | 102.235 | R270
C33 | 680p | C0805 | rcl | 129.8575 | 33.9725 | R90
C34 | 10u | PANASONIC_B | rcl | 20.32 | 111.76 | R180
C35 | 100n | C0805 | rcl | 41.275 | 111.76 | R0
C36 | 100n | C0805 | rcl | 46.6725 | 102.235 | R270
C37 | 100u | PANASONIC_D | rcl | 133.35 | 74.93 | R270
C38 | 100u | PANASONIC_D | rcl | 133.35 | 113.9825 | R270
C39 | 100u | PANASONIC_D | rcl | 133.35 | 105.41 | R90
C41 | 100n | C0805 | Resistor | 129.8575 | 80.645 | R90
C42 | 100n | C0805 | Resistor | 126.6825 | 104.775 | R270
C43 | 100n | C0805 | Resistor | 128.5875 | 104.775 | R270
C44 | 100n | C0805 | rcl | 64.77 | 8.89 | R90
C45 | 100n | C0805 | rcl | 68.58 | 8.89 | R90
C46 | 22n | C0805 | rcl | 27.94 | 76.2 | R270
C47 | 100n | C0805 | rcl | 40.64 | 74.93 | R0
C48 | 100p | C0805 | rcl | 34.29 | 85.09 | R0
C49 | 100n | C0805 | rcl | 41.91 | 64.77 | R90
C50 | 1n | C1812 | rcl | 3.175 | 83.82 | R90
C51 | 10u | PANASONIC_B | rcl | 41.91 | 90.17 | R270
C52 | 330n | C1812 | rcl | 8.89 | 76.835 | R180
C53 | 100n | C0805 | rcl | 38.1 | 90.17 | R90
C54 | 100u | PANASONIC_D | rcl | 121.92 | 61.595 | R270
C55 | 100n | C0805 | rcl | 117.475 | 49.53 | R270
C56 | 100n | C0805 | Resistor | 91.44 | 93.98 | R180
C59 | 47n | C0805 | Resistor | 97.79 | 84.455 | R180
C60 | 100n | C0805 | rcl | 134.62 | 84.1375 | R270
C61 | 100n | C0805 | rcl | 132.08 | 84.1375 | R270
C62 | 100n | C0805 | rcl | 50.8 | 29.5275 | R0
C63 | 100u | PANASONIC_D | rcl | 10.16 | 6.35 | R90
C64 | 100u | PANASONIC_D | rcl | 10.16 | 27.305 | R90
C65 | 100u | PANASONIC_D | rcl | 10.16 | 48.26 | R90
C66 | 100u | PANASONIC_D | rcl | 33.02 | 20.32 | R270
C67 | 100u | PANASONIC_D | rcl | 33.02 | 41.275 | R270
C68 | 100n | C0805 | rcl | 71.4375 | 17.78 | R90
D1 | SS54-HF | DO214AC | diode | 140.335 | 121.285 | R0
D2 | SS54-HF | DO214AC | diode | 107.95 | 82.55 | R90
D4 | RGF1G | DO214AC | diode | 66.04 | 123.825 | R180
D6 | RGF1G | DO214AC | diode | 94.2975 | 10.16 | R0
D7 | 1N4148WS | SOD-323 | Diodes | 112.0775 | 35.56 | R270
D8 | SML4757A | SMB | diode | 133.6675 | 7.62 | R0
D9 | SML4757A | SMB | diode | 112.0775 | 7.62 | R0
D10 | SS54-HF | DO214AC | diode | 126.1452625 | 10.0622375 | R90
D12 | RGF1G | DO214AC | diode | 146.05 | 11.43 | R90
D13 | RGF1G | DO214AC | diode | 140.335 | 7.62 | R180
D14 | RGF1G | DO214AC | diode | 119.6975 | 7.62 | R180
D15 | RGF1G | DO214AC | diode | 104.4575 | 10.16 | R0
D16 | 1N4148WS | SOD-323 | Diodes | 132.3975 | 35.56 | R270
IC1 | 555 | SO08 | SparkFun-IC-Special-Function | 119.0625 | 41.91 | R270
IC2 | 74HC4053D | SO16 | 74xx-eu | 49.53 | 19.685 | R270
IC3 | LM358MX | SO08 | linear | 10.16 | 106.68 | R180
IC4 | 555 | SO08 | SparkFun-IC-Special-Function | 139.3825 | 41.91 | R270
IC5 | LM358MX | SO08 | linear | 25.4 | 106.68 | R180
IC6 | LM358MX | SO08 | linear | 40.64 | 106.68 | R180
IC7 | 74HC4053D | SO16 | 74xx-eu | 66.04 | 24.13 | R180
IC8 | SE555DRG4 | SO08 | SparkFun-IC-Special-Function | 33.02 | 80.01 | R180
IC9 | AS7805ADTR | DPAC_NEU | linear | 33.02 | 67.31 | R90
IC10 | MIC4420M | SO-08 | transistor-power | 33.02 | 90.17 | R90
IC11 | LM1117MPX | SOT223 | v-reg | 130.81 | 52.07 | R0
IC12 | LM1117MPX | SOT223 | v-reg | 112.395 | 52.07 | R0
J3 | 618009211821 | Wurth_Connectors_WR-DSUB |  | 91.44 | 135.89 | R180
L1 | 100uh | WE-CHSA_1212 | Wurth_Automotive_WE-CHSA | 19.05 | 71.12 | R90
L2 | 220uh | WE-CHSA_1212 | Wurth_Automotive_WE-CHSA | 102.87 | 97.155 | R270
Q1 | IRFR3410TRPBF | DPAK | transistor_test | 101.6 | 119.38 | R0
Q2 | IRFR3410TRPBF | DPAK | transistor_test | 66.04 | 115.57 | R0
Q3 | IRFR3410TRPBF | DPAK | transistor_test | 54.61 | 115.57 | R0
Q5 | IPD60R180P7SAUMA1 | DPAK | transistor_test | 19.05 | 85.09 | R180
Q6 | IRFR3410TRPBF | DPAK | transistor_test | 133.6675 | 22.86 | R180
Q7 | IRFR3410TRPBF | DPAK | transistor_test | 104.4575 | 22.86 | R180
Q8 | IRFR3410TRPBF | DPAK | transistor_test | 113.3475 | 22.86 | R180
Q9 | IRFR3410TRPBF | DPAK | transistor_test | 94.2975 | 22.86 | R180
R1 | 4k7 | R0805 | rcl | 90.805 | 116.84 | R90
R2 | 100k | R0805 | rcl | 71.12 | 108.2675 | R0
R3 | 1m | R0805 | rcl | 90.805 | 40.64 | R0
R4 | 100k | R0805 | rcl | 56.1975 | 108.2675 | R0
R5 | 100k | R0805 | rcl | 5.08 | 29.845 | R270
R6 | 100k | R0805 | rcl | 5.08 | 8.89 | R90
R7 | 4k7 | R0805 | rcl | 93.98 | 124.46 | R0
R8 | 100k | R0805 | rcl | 5.08 | 50.8 | R270
R9 | 100k | R0805 | rcl | 103.1875 | 110.49 | R0
R10 | 100k | R0805 | rcl | 38.1 | 38.735 | R90
R11 | 4k7 | R0805 | rcl | 93.345 | 116.84 | R90
R12 | 120 | R0805 | rcl | 111.125 | 45.72 | R0
R13 | 10 | R0805 | rcl | 99.06 | 110.49 | R180
R14 | 10 | R0805 | rcl | 65.0875 | 108.2675 | R180
R15 | 10 | R0805 | rcl | 52.3875 | 107.315 | R90
R16 | 10k | R0805 | rcl | 6.35 | 20.32 | R180
R18 | 10k | R0805 | rcl | 6.35 | 41.275 | R180
R19 | 10k | R0805 | rcl | 6.35 | 62.23 | R180
R20 | 10k | R0805 | rcl | 36.83 | 27.305 | R0
R21 | 4k7 | R0805 | rcl | 87.9475 | 22.86 | R270
R22 | 4k7 | R0805 | rcl | 85.4075 | 22.86 | R270
R23 | 1k | R0805 | rcl | 54.2925 | 92.3925 | R180
R24 | 1k | R0805 | rcl | 54.2925 | 94.9325 | R180
R25 | 1k | R0805 | rcl | 69.5325 | 97.4725 | R0
R26 | 100k | R0805 | rcl | 38.1 | 17.78 | R90
R27 | 10k | R0805 | rcl | 36.83 | 6.35 | R0
R28 | 330 | R0805 | rcl | 129.8575 | 38.1 | R90
R29 | 10k | R0805 | rcl | 134.3025 | 42.545 | R90
R30 | 330 | R0805 | rcl | 136.8425 | 36.83 | R270
R31 | 10 | R0805 | rcl | 136.2075 | 31.75 | R270
R32 | 10k | R0805 | rcl | 144.145 | 30.48 | R0
R33 | 4k7 | R0805 | rcl | 140.0175 | 30.48 | R180
R35 | 1k | R0805 | rcl | 15.24 | 111.76 | R180
R36 | 10k | R0805 | rcl | 4.1275 | 103.505 | R270
R37 | 4k7 | R0805 | rcl | 5.08 | 107.95 | R0
R38 | 1k | R0805 | rcl | 16.1925 | 97.79 | R270
R39 | 1M | R0805 | rcl | 16.1925 | 107.6325 | R270
R40 | 1k | R0805 | rcl | 29.21 | 102.235 | R90
R43 | 10k | R0805 | rcl | 13.97 | 107.6325 | R270
R44 | 330 | R0805 | rcl | 109.5375 | 38.4175 | R90
R45 | 10k | R0805 | rcl | 113.9825 | 42.545 | R270
R46 | 330 | R0805 | rcl | 117.1575 | 36.83 | R270
R47 | 10 | R0805 | rcl | 115.8875 | 31.75 | R270
R48 | 10k | R0805 | rcl | 123.825 | 30.48 | R0
R49 | 4k7 | R0805 | rcl | 119.6975 | 30.48 | R180
R53 | 10 | R0805 | rcl | 106.9975 | 31.75 | R270
R54 | 100k | R0805 | rcl | 103.1875 | 30.48 | R0
R55 | 100k | R0805 | rcl | 112.0775 | 31.4325 | R270
R56 | 100k | R0805 | rcl | 132.3975 | 31.4325 | R270
R57 | 1k | R0805 | rcl | 30.48 | 111.76 | R180
R58 | 10k | R0805 | rcl | 19.3675 | 103.505 | R270
R59 | 4k7 | R0805 | rcl | 20.32 | 107.95 | R0
R61 | 1k | R0805 | rcl | 31.4325 | 97.79 | R270
R62 | 1M | R0805 | rcl | 31.4325 | 107.6325 | R270
R63 | 1k | R0805 | rcl | 13.97 | 102.235 | R90
R65 | 10k | R0805 | rcl | 29.21 | 107.6325 | R270
R66 | 0R1 | R1206 | rcl | 33.02 | 118.11 | R90
R67 | 0R1 | R1206 | rcl | 17.78 | 118.11 | R90
R68 | 1k | R0805 | rcl | 45.72 | 111.76 | R180
R69 | 10k | R0805 | rcl | 34.6075 | 103.505 | R270
R70 | 4k7 | R0805 | rcl | 35.56 | 107.95 | R0
R71 | 1k | R0805 | rcl | 46.6725 | 97.79 | R270
R72 | 1M | R0805 | rcl | 46.6725 | 107.6325 | R270
R73 | 1k | R0805 | rcl | 44.45 | 102.235 | R90
R76 | 10k | R0805 | rcl | 44.45 | 107.6325 | R270
R77 | 0R1 | R1206 | rcl | 48.26 | 118.11 | R90
R78 | 10k | R0805 | rcl | 50.165 | 45.4025 | R180
R79 | 10k | R0805 | rcl | 93.98 | 120.65 | R180
R82 | 100k | R0805 | rcl | 72.0725 | 39.6875 | R90
R83 | 100 | R0805 | rcl | 25.0825 | 134.62 | R0
R84 | 15k | R0805 | rcl | 31.75 | 74.93 | R180
R87 | 10 | R0805 | rcl | 25.4 | 90.17 | R180
R89 | 3k | R0805 | rcl | 97.79 | 81.915 | R180
R90 | 1k | R0805 | rcl | 91.44 | 79.375 | R90
R91 | 18k | R0805 | rcl | 93.98 | 79.375 | R270
R92 | 330 | R0805 | rcl | 69.5325 | 94.9325 | R0
R93 | 330 | R0805 | rcl | 69.5325 | 92.3925 | R0
R94 | 330 | R0805 | rcl | 69.5325 | 89.8525 | R0
R95 | 1k | R0805 | rcl | 54.2925 | 82.2325 | R180
R96 | 1k | R0805 | rcl | 54.2925 | 79.6925 | R180
R97 | 1k | R0805 | rcl | 54.2925 | 84.7725 | R180
R98 | 330 | R0805 | rcl | 54.2925 | 87.3125 | R180
R99 | 10 | R0805 | rcl | 96.8375 | 31.75 | R270
R100 | 100k | R0805 | rcl | 93.0275 | 30.48 | R0
R101 | 330 | R0805 | rcl | 69.5325 | 87.3125 | R0
R102 | 4k7 | R0805 | rcl | 44.45 | 79.375 | R270
R103 | 120 | R0805 | rcl | 142.24 | 56.515 | R180
R106 | 10 | R0805 | rcl | 25.4 | 88.265 | R180
T1 | BC847 | SOT23 | transistor | 132.3975 | 39.37 | R0
T2 | BC847 | SOT23 | transistor | 140.6525 | 34.29 | R180
T3 | BC847 | SOT23 | transistor | 112.0775 | 39.37 | R0
T4 | BC847 | SOT23 | transistor | 120.3325 | 34.29 | R180
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

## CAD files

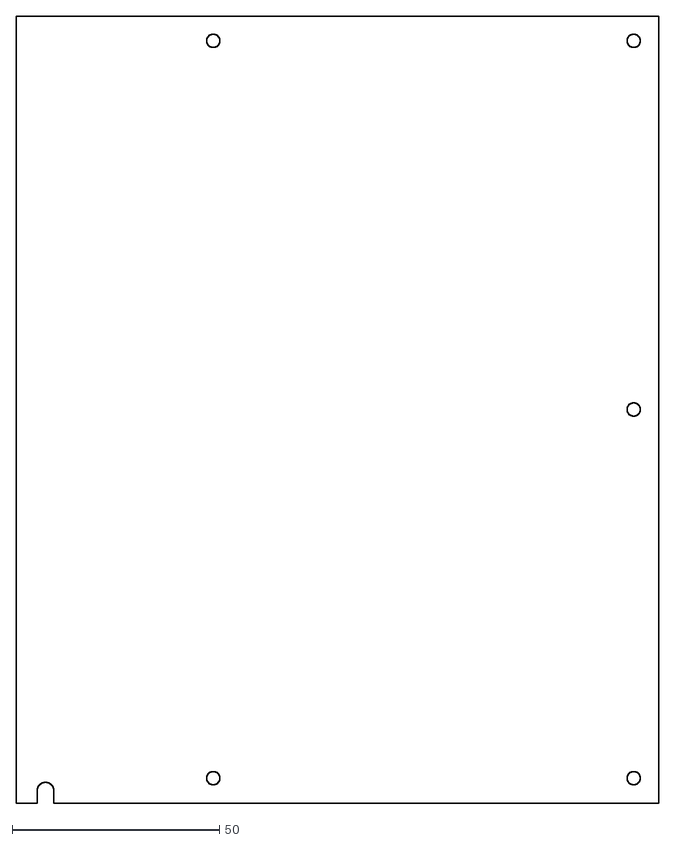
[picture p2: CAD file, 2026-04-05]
2LabsToGo-Eco-Hardware/3D-Parts/DXF-panels/back_humidity-control.dxf
155.0 x 190.0

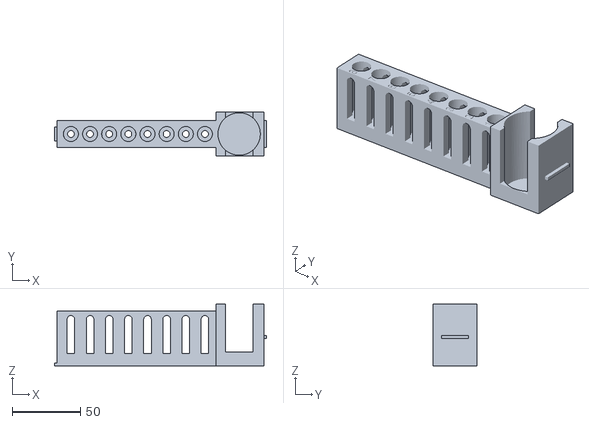
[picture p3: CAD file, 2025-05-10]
2LabsToGo-Eco-Hardware/3D-Parts/STL/autosampler/autosampler_vialrack_ver2.stl
155.0 x 32.0 x 45.0

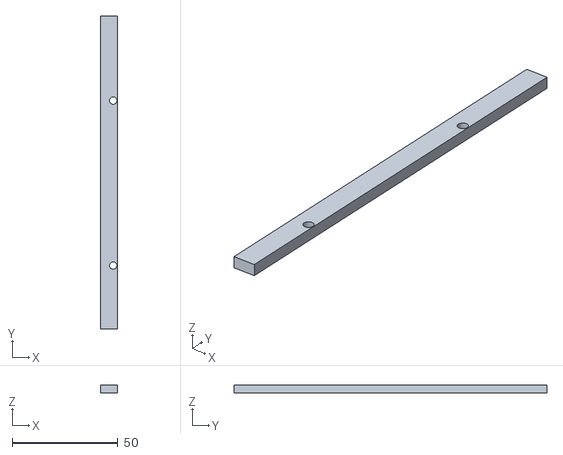
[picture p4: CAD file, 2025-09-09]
2LabsToGo-Eco-Hardware/3D-Parts/STL/electronic-box/electronic_box_frame-part2.stl
8.00 x 148.0 x 4.00

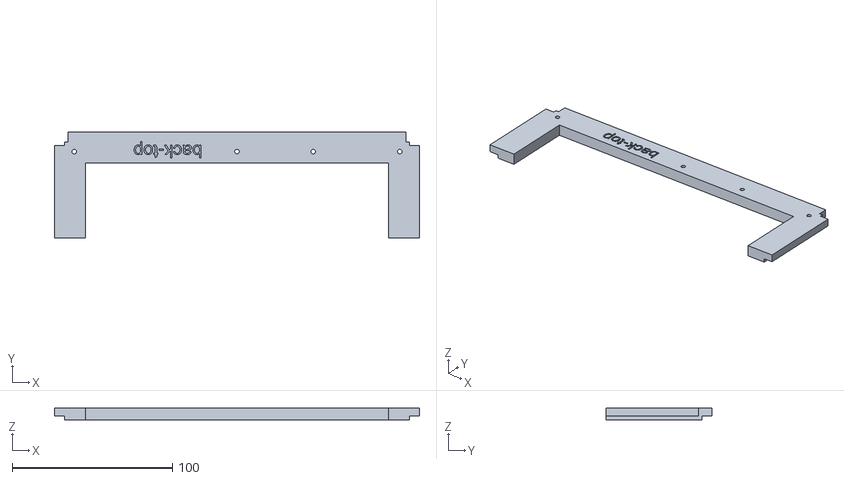
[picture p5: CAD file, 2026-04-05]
2LabsToGo-Eco-Hardware/3D-Parts/STL/frames/frame_back_top.stl
227.6 x 66.3 x 7.50

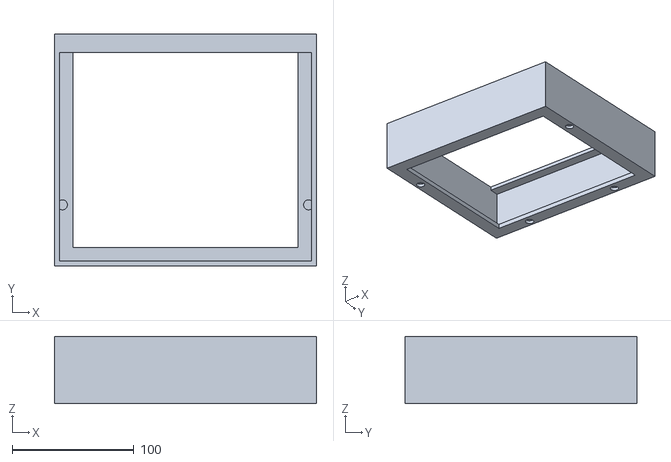
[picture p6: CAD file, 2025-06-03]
2LabsToGo-Eco-Hardware/3D-Parts/STL/humidity-control/front-extension.stl
215.0 x 190.0 x 55.0

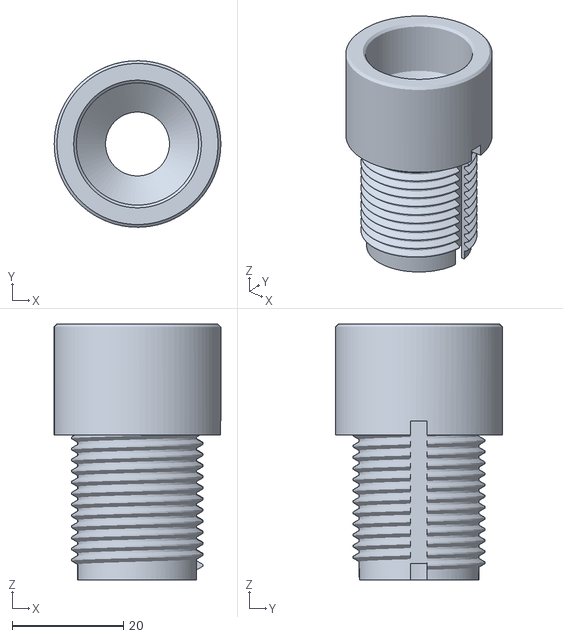
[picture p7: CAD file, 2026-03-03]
2LabsToGo-Eco-Hardware/3D-Parts/STL/nebulizer/nebulizer_atomizer_part-1.stl
30.0 x 30.0 x 46.1

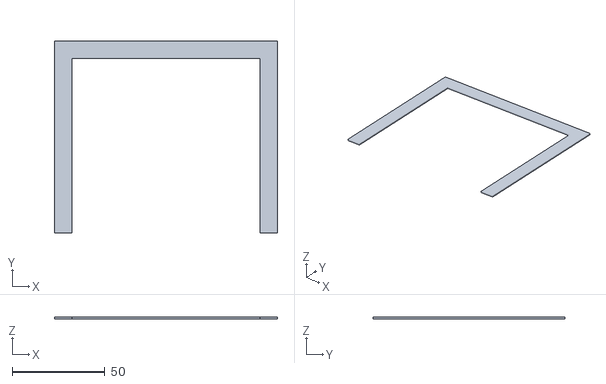
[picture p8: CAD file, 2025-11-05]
2LabsToGo-Eco-Hardware/3D-Parts/STL/plate-holder/multifunctional_plate_holder-cover_development_glass-plate_cover.stl
120.0 x 103.4 x 1.00

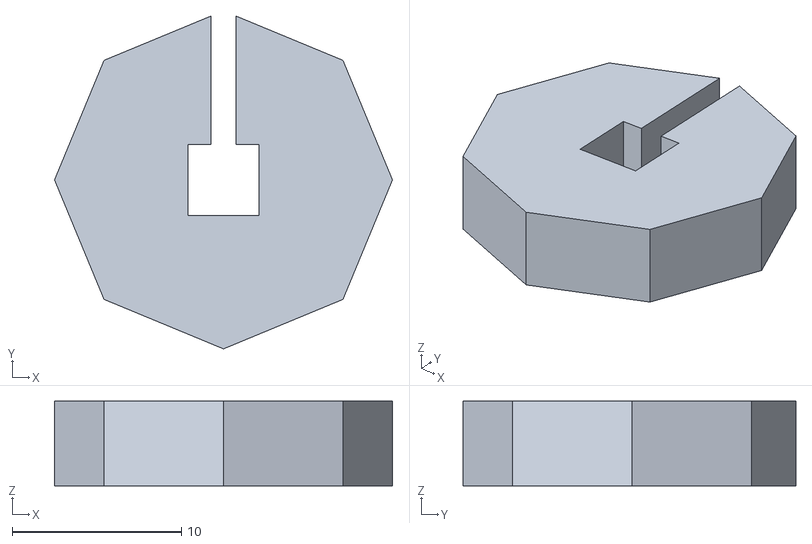
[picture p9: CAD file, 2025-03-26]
2LabsToGo-Eco-Hardware/3D-Parts/STL/tools/needle-wrench_round.stl
20.0 x 19.7 x 5.00

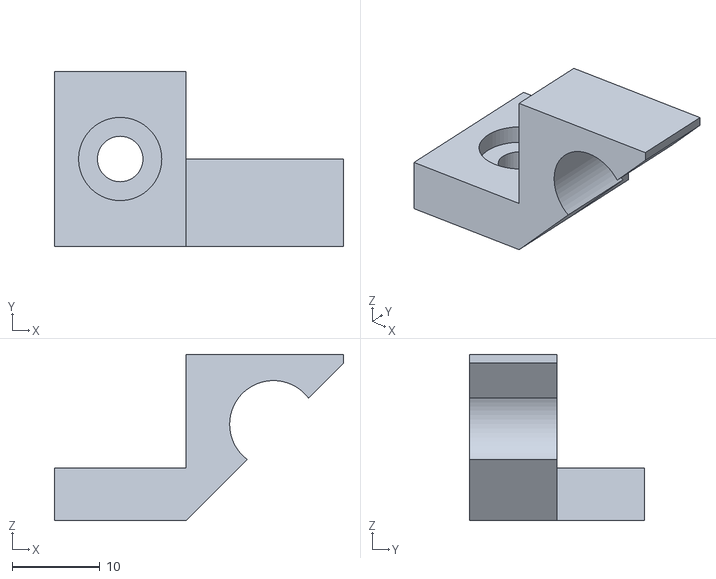
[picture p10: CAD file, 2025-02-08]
2LabsToGo-Eco-Hardware/3D-Parts/STL/x-axis/x-axis_cable_guide_top_right.stl
33.0 x 20.0 x 19.0

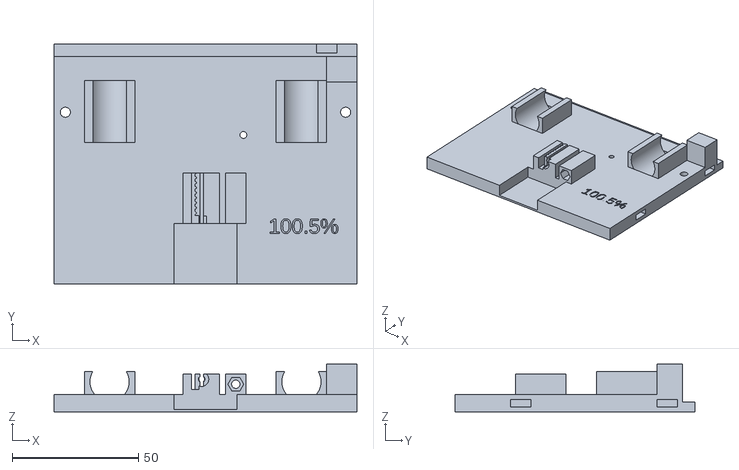
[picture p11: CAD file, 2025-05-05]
2LabsToGo-Eco-Hardware/3D-Parts/STL/y-axis/y-axis_cart_tensioner.stl
120.0 x 95.0 x 19.0

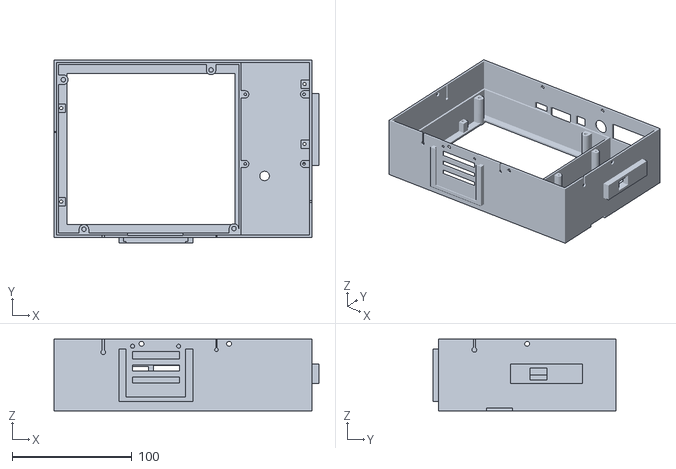
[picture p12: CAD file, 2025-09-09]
2LabsToGo-Eco-Hardware/3D-Parts/STL/electronic-box/electronic_box.stl
221.0 x 152.4 x 60.0

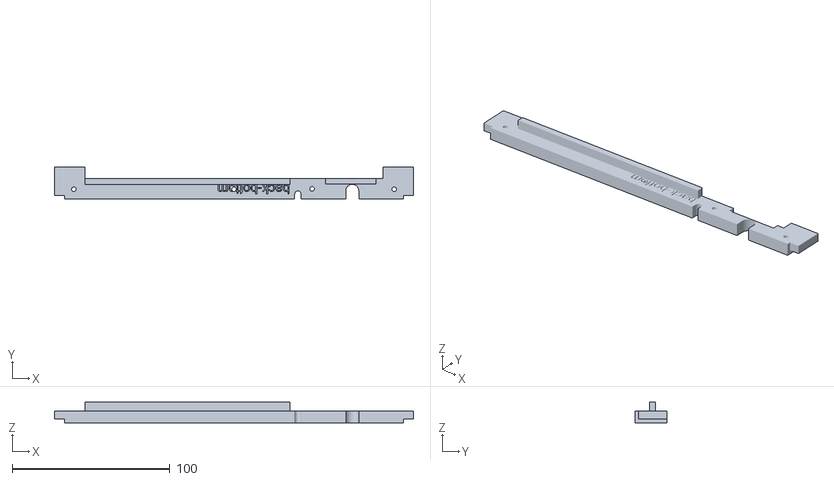
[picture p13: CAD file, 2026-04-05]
2LabsToGo-Eco-Hardware/3D-Parts/STL/frames/frame_back_buttom.stl
227.6 x 20.0 x 13.0

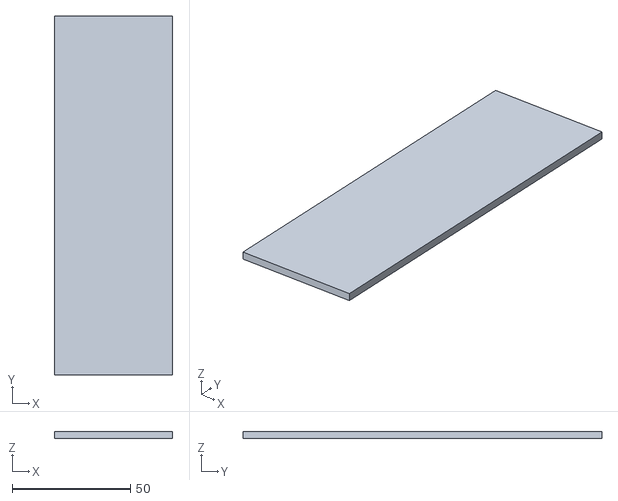
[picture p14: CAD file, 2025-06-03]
2LabsToGo-Eco-Hardware/3D-Parts/STL/humidity-control/humidity_control_box-lid.stl
50.0 x 152.0 x 3.00

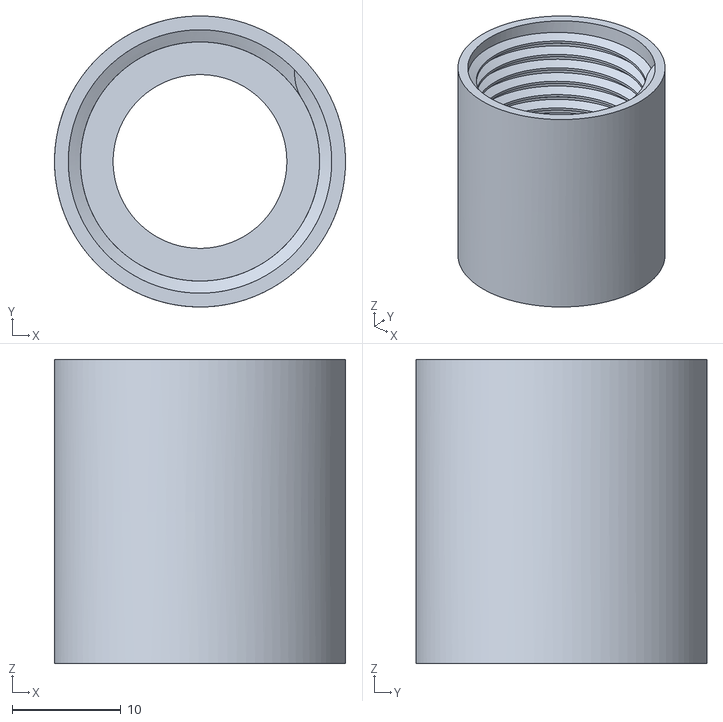
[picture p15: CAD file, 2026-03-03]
2LabsToGo-Eco-Hardware/3D-Parts/STL/nebulizer/nebulizer_atomizer_part-2.stl
26.8 x 26.8 x 28.0

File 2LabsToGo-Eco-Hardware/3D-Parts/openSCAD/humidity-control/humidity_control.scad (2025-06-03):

//humidity control 2LabsToGo-Eco

$fn=80;
h=38; //box height
hf=28; //fan height

box();
//lid();
//drawer();
//drawer_handle();
//front_extension();

module box() {
difference() {
    union() {
        cube([60, 190, 3]);
        translate([10, 20+7, 3]) cube([47, 4, h]);
        translate([10, 20+7, 3]) cube([4, 155-7, h]);
        translate([60-4, 20+7, 3]) cube([4, 155-7, h]);
        translate([10, 145+30, 3]) cube([50, 4, h]);
        
        //z1 motor cover
        translate([32.5-21-2, 0, 3]) cube([2, 28, 10]);
       translate([32.5+21, 0, 3]) cube([2, 28, 10]); 
        translate([32.5-21-2, 26, 3]) cube([44, 2, 10]);
    }
    //cutouts
    //cutout z1 spindle
       translate([32.5, 5.1, -1]) cylinder(d=8.2, h=5);
       translate([32.5-8.2/2, -1, -1]) cube([8.2, 6.1, 5]);
    //cutout suction opening
    translate([10+4, 134, -1]) cube([42, 30, 6]);
    //cutout fan
    translate([35, 30+21, -1]) cylinder(d=38, h=5);
    //holes fan screws
    translate([10+3+4+2, 30+21-16, -1]) cylinder(d=3.3, h=6);
    translate([10+3+4+32+2, 30+21-16, -1]) cylinder(d=3.3, h=6);
    translate([10+3+4+2, 30+21+16, -1]) cylinder(d=3.3, h=6);
    translate([10+3+4+32+2, 30+21+16, -1]) cylinder(d=3.3, h=6);
    //cutout drawer
    rotate([90, 0, 90]) translate([30+20+23, 3, 55])  cutout_drawer(); 
    //holes for screws
    for (i=[0:2])
    translate([6, 6+i*89, -1]) cylinder(d=3.2, h=5);
    translate([60-2, 6, -1]) cylinder(d=3.2, h=5);
    translate([60-6, 190-6, -1]) cylinder(d=3.2, h=5);
    }
}

module lid() {
    cube([50, 155+3-6, 3]);
}

module drawer() {
    difference() {
        linear_extrude(height = 46, scale = 1) 
    polygon(points=[[0,0],[0,hf-0.3],[60-0.3,h-0.2], [60-0.3,0]]);
        translate([2, 2, 2])
        linear_extrude(height = 46-4, scale = 1)  polygon(points=[[0,0],[0,hf-6],[60,h-6], [60,0]]);
   
    a=(h-hf)/60; //arctan
    b=a*180/3.14;  //rad in °
    //1.5 mm slits
    for(x=[3:3:42])
    translate([2, hf-5, x]) rotate([0, 0, b]) cube([20, 6, 1.5]);
    //1 mm slits
    //for(x=[3:2:44])
    //translate([2, hf-5, x]) rotate([0, 0, b]) cube([20, 6, 1]); 
    }
    translate([60-2.2, h-2.2, 0]) cube([2, 2, 46 ]);
}

module cutout_drawer() {
    linear_extrude(height = 10, scale = 1) 
    polygon(points=[[0,0],[0,h],[60,h], [60,0]]);
}

module drawer_handle() {
    translate([95-3-3+3, -3, 0]) cube([3, 66, h+3]);
    translate([95-3-3+3, -3, 13]) cube([10, 66, 3]);
    translate([95-3+10, -3, 14]) rotate([-90, 0, 0]) cylinder(d=6, h=66);
}

module fan( ) {
    difference() {
    hull() {
        translate([3, 3, 0]) cylinder(d=6, h=28);
        translate([40-3, 3, 0]) cylinder(d=6, h=28);
        translate([3, 40-3, 0]) cylinder(d=6, h=28);
        translate([40-3, 40-3, 0]) cylinder(d=6, h=28);
    }
    translate([20, 20, -1]) cylinder(d=38, h=42);
}
translate([20, 20, 0]) cylinder(d=12, h=28);
$fn=120;

translate([20, 20, 0])
linear_extrude(height = 28, center = false, convexity = 10, twist = 360, $fn = 100)
translate([5, 0, 0])
square([13, 1]);

translate([20, 20, 0]) rotate([0, 0, 120])
linear_extrude(height = 28, center = false, convexity = 10, twist = 360, $fn = 100)
translate([5, 0, 0])
square([13, 1]);

translate([20, 20, 0]) rotate([0, 0, 240])
linear_extrude(height = 28, center = false, convexity = 10, twist = 360, $fn = 100)
translate([5, 0, 0])
square([13, 1]);

}

module front_extension() {
    difference() {
    union() {
        cube([215, 190, 5]);
        cube([4, 190, 55]);
        cube([215, 4, 55]); 
        translate([215-4, 0, 0]) cube([4, 190, 55]);    
        translate([0, 190-4, 4]) cube([215, 4, 55-4]);
        translate([0, 190-15, 55-4]) cube([215, 15, 4]);
        }
    translate([15, 15, -1]) cube([215-2*15, 190-2*15, 7]);
    //cutout magnets
        translate([50, 190-6.5, 0]) cylinder(d1=9, d2=8.2, h=3.2);
        translate([215-50, 190-6.5, 0]) cylinder(d1=9, d2=8.2, h=3.2);
        translate([50, 190-6.5, 5-1.5]) cylinder(d=9, h=4);
        translate([215-50, 190-6.5, 5-1.5]) cylinder(d=9, h=4);
        
        translate([6.5, 50, 0]) cylinder(d1=9, d2=8.2, h=3.2);
        translate([215-6.5, 50, 0]) cylinder(d1=9, d2=8.2, h=3.2);
        translate([6.5, 50, 5-1.5]) cylinder(d=8.2, h=4);
        translate([215-6.5, 50, 5-1.5]) cylinder(d=8.2, h=4);
    }
}

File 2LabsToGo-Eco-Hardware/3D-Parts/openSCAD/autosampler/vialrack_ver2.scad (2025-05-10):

//your vial data, correct respectively
d=11;  //vial OD plus 0.5 mm
d1=13; //vial cap OD + 0.5 mm
h=42.2;  //vial height including cap plus 0.5 mm
n=8;  //number of sample vials without rinsing vial
p=8;  //spindle pitch

$fn=80;

b=6;

vial_rack();
//test vial
//color("white", 0.6) {translate([10, 10, 3-2]) cylinder(d=d, h=h); 
    //translate([10, 10, 3+h-3]) cylinder(d=d1, h=3);
    //}

//color("blue", 1.9) { translate([58, 9.5, -2]) import("vialrack_holder.stl"); }

//poly();

module vial_rack() {
difference(){
    D=4.5;
union() {
difference() {
    cube([116, 20, 40]);
    //cut bottom
    //translate([-2, -7, -6]) cube([160, 40, 8]); 
    
    //Screw holes/slit
    translate([20+4.5, 20-D, -3]) cylinder(d=6.5, h=6);
    translate([20+10, 20-D, -3]) cylinder(d=6.5, h=6);
    translate([20+4.5, 20-D-6.5/2, -3]) cube([5.1, 6.5, 6]);    
    
    translate([20+14.5, D, -3]) cylinder(d=6.5, h=6);
    translate([20+14.5+5.1, D, -3]) cylinder(d=6.5, h=6);
    translate([20+14.5, D-6.5/2, -3]) cube([5.1, 6.5, 6]);
    
    translate([20+5+70, 20-D, -3]) cylinder(d=6.5, h=6);
    translate([20+5+70+5.1, 20-D, -3]) cylinder(d=6.5, h=6);
    translate([20+5+70, 20-D-6.5/2, -3]) cube([5.1, 6.5, 6]);
    
    translate([20+1.5+84, D, -3]) cylinder(d=6.5, h=6);
    translate([20+1.5+84+5.1, D, -3]) cylinder(d=6.5, h=6);
    translate([20+1.5+84, D-6.5/2, -3]) cube([5.1, 6.5, 6]);
          
    //cutout vials
    for(x = [10 : 14: 14*n-4])
    translate([x, 10, 1+b+2]) cylinder(d=d, h=h-4);
    //for(z = [10 : 14: 14*n-4])
    //translate([z-d/2, 10, 1+b+2]) cube([d, d, 35]);
    
    //cutout oben Anschlag
    /*for(c = [10 : 14: 14*n-4])
    translate([c-d1/2, -2, h-7+6-2+b+2]) cube([d1, 24, 2]);
    for(f = [10 : 14: 14*n-4])
    translate([f-d/2, -2, 30-2+b]) cube([d, 24, 11.5]);
    for(g = [10 : 14: 14*n-4])
    translate([g, 10, -1]) cylinder(d=5, h=12);
    */
    //cutout back view
    for(f = [10 : 14: 14*n-4])
    translate([f-2.5-0.25, -7, 5-2+4+2]) cube([5.5, 30, 30-4.75]);
    
    
    //cutout rounding the walls
    for(f = [10 : 14: 14*n-4])
    translate([f-d/2+d/2, -7, 30-2+b]) rotate([-90, 0, 0]) cylinder(d=5.5, h=30);
    /*
    for(f = [10 : 14: 14*n-4])
    //translate([f, -7, h-7+6-2+b+2]) rotate([-90, 0, 0]) cylinder(d=d1, h=30, $fn=6);
    for(f = [10 : 14: 14*n-4])
    translate([f, -7, h-7+6-2+b+2]) rotate([-90, 0, 0]) cylinder(d=d1, h=30, $fn=6);
    
    for(f = [10 : 14: 14*n-4])
    //translate([f, -7, h+1-2+b]) rotate([-90, 0, 0]) cylinder(d=d1, h=30, $fn=6);
    //#translate([f, -7, h+1-2+b]) poly();
    
    for(c = [10 : 14: 14*n-4])
    translate([c-d1/2, 21, 49.2]) poly();
    //translate([17.5, 21, 49.2]) poly();
    //c-d1/2, -2, h-7+6-2+b
    */
    //holes for the needle
    //for(a = [10 : 14: 14*n-4])
    //translate([a, 10, 46]) cylinder(d=8, h=15);
    for(g = [10 : 14: 14*n-4])
    translate([g, 10, -1]) cylinder(d=5, h=12);
}
//body rinsing vial
difference() {
    translate([116, -6, 0]) cube([35, 32, 45]);
    //translate([-1, -7, -6]) cube([160, 35, 8]); 
    //cutout bottom for vial
    //#translate([133, 10, 3-2]) cylinder(d=30, h=50);
    translate([133, 10, 3-2]) cylinder(d=31, h=60);
    //translate([133-31/2, 10, 10]) cube([31, 18, 60]);
    //cutout top vial
    //#translate([133, 10, 56-12]) cylinder(d=30, h=7);
    //translate([133-30/2, 10, 56-10]) cube([30, 18, 7-2]);
    //translate([133-30/2, -9, 10]) cube([30, 36, 36]);
    //translate([132-5, -9, 1]) cube([10, 36, 35]);
    
    //hole for needle rinsing vial
    //translate([133, 10, 39]) cylinder(d=20, h=20);
    translate([133-10, -10, 10]) cube([20, 40, 45]);
    }
}
//translate([-1, -6, 48.6])cube([131.36, 9, 8]);
}
//support for positioning
translate([-2, 5, 0]) cube([3, 10, 2]);
//translate([150, 10, 23]) sphere(d=3.4);
translate([150, 0, 20]) cube([3, 20, 2]);
}

module poly() {
    rotate([90, 0, 0])
    linear_extrude(height = 22, scale = 1)
    
    polygon([[0,0],[3.25,5.629-1.5], [13-3.25,5.629-1.5], [13,0]]);
    //polygon([[0,0],[100,0],[130,50],[30,50]],[[1,0,3,2]]);
}

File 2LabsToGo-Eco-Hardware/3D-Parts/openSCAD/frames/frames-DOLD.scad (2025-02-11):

//frames

$fn=80;
y1=102;
y2=148;
x=215;
z=210;
b=13;
pd=6.3; //profile depth

//right_front();
//right_back();
//left_front();
//left_back();
back();
//top_front();
//top_front_fan();
//top_back();
//top_back_cable_channel();
//top_back_cover();
//board_cover();
//translate([55, 13, 12.5]) board_cover(); 
//front();
//cover_z_motor();
//cable_clip_1();
//cable_clip_2();
//cable_clip_3();
//cable_clip_alu();
//color("blue", 0.5) {rotate([-90, 0, 90]) translate([8, -15, -80]) cable_support();} //electronic box
//cable_support();
//translate([202, 10, 14.5]) rotate([0, 180, 0]) cable_support();
//scratching_aid_magnets_front();

//bohrschablone();

module top_front_fan() {
difference() {
import("frame_top_front.stl");
    translate([71.75-0.5, 7.5, -1]) cube([81, 80, 10]);
}
}


module bohrschablone() {
    w=y1+2*pd;
    h=z+2*pd;
    difference() {
        translate([-5, -5, 0])cube([230, 130, 8]);
        translate([0, 0, 5]) cube([260, 130, 5]);
        
        n1=(h-2*pd)/2-6;  //h-2*pd = y1 or y2
        n2=(w-2*pd)/2-6;
        
        for (i=[0:2])
        translate([6, 6+i*n1, -4]) cylinder(d=3.2, h=10);
        for (i=[0:2])
        translate([w-2*pd-6, 6+i*n1, -4]) cylinder(d=3.2, h=10);
        for (i=[0:2])
        translate([6+i*n2, 6, -4]) cylinder(d=3.2, h=10); 
        //for (i=[0:2])
        //translate([6+i*n2, h-2*pd-6, -4]) cylinder(d=2.9, h=10); 
        
    w=y2+2*pd;
    h=z+2*pd;
    n3=(h-2*pd)/2-6;  //h-2*pd = y1 or y2
    n4=(w-2*pd)/2-6;
        for (i=[0:2]) //links
        translate([6, 6+i*n3, -4]) cylinder(d=3.2, h=10);
        for (i=[0:2])  //rechts
        translate([w-2*pd-6, 6+i*n3, -4]) cylinder(d=3.2, h=10);
        for (i=[0:2])  //unten
        translate([6+i*n4, 6, -4]) cylinder(d=3.2, h=10); 
        //for (i=[0:2])  //oben
        //translate([6+i*n2, h-2*pd-6, -4]) cylinder(d=2.9, h=10);
    //h=z+2*pd-20;
    w1=x+2*pd;
    n5=(h-2*pd)/2-6;  //h-2*pd = y1 or y2
    n6=(w1-2*pd)/2-6; 
        for (i=[0:2]) //links
        translate([6, 6+i*n5, -4]) cylinder(d=3.2, h=10);
        for (i=[0:2])  //rechts
        translate([w1-2*pd-6, 6+i*n5, -4]) cylinder(d=3.2, h=10);
        for (i=[0:2])  //unten
        translate([6+i*n6, 6, -4]) cylinder(d=3.2, h=10); 
    }
}

module frame(w, h, d) {
    difference() {
        translate([-pd, -pd, 0]) cube([w, h, d]);
        translate([b, b, -4]) cube([w-2*pd-2*b, h-2*pd-2*b, 12]);
        //cutout edges
        translate([-pd, -pd, -1]) cube([pd+2.2, pd, 8]);
        translate([-pd, -pd, -1]) cube([pd, pd+2.2, 8]);
        translate([w-2*pd-2.2, -pd, -1]) cube([pd+2.2, pd, 8]);
        translate([w-2*pd, -pd, -1]) cube([pd, pd+2.2, 8]);
        translate([w-2*pd-2.2, h-2*pd, -1]) cube([pd+2.2, pd, 8]);
        translate([w-2*pd, h-2*pd-2.2, -1]) cube([pd, pd+2.2, 8]);
        
        translate([-pd, h-2*pd-2.2, -1]) cube([pd, pd+2.2, 8]);
        translate([-pd, h-2*pd, -1]) cube([pd+2.2, pd, 8]);
    //holes for screws
    n1=(h-2*pd)/2-6;  //h-2*pd = y1 or y2
    n2=(w-2*pd)/2-6;  //w-2*pd = x
    for (i=[0:2])
        translate([6, 6+i*n1, -4]) cylinder(d=2.9, h=10);
    for (i=[0:2])
        translate([w-2*pd-6, 6+i*n1, -4]) cylinder(d=2.9, h=10);
    for (i=[0:2])
        translate([6+i*n2, 6, -4]) cylinder(d=2.9, h=10); 
    for (i=[0:2])
        translate([6+i*n2, h-2*pd-6, -4]) cylinder(d=2.9, h=10);
    }
} 

module left_front() {  //korrigiert
    frame(y1+2*pd, z+2*pd, 5);
    //cable channel
    translate([b-4, b, 5]) cube([4, z-2*b, 7.5]);
    translate([b-4, z-b, 5]) cube([y1-2*b+4, 4, 7.5]);
    //translate([y1-b, b-4, 5]) cube([4, z-2*b+4+4, 7.5]);
    //translate([b-4, b-4, 5]) cube([y1-2*b+4, 4, 7.5]);
    string1 = str("left-front");
    translate ([10, 3, 4]) rotate([0, 0, 0])
    linear_extrude(2.0) text(string1, size = 6, direction = "ltr", spacing = 1 );
}

module right_front() {   //korrigiert
    frame(y1+2*pd, z+2*pd, 5);
    //cable channel
    translate([y1-b, b-4, 5]) cube([4, z-2*b+4+4, 7.5]);
    translate([b-4, z-b, 5]) cube([y1-2*b+4+4, 4, 7.5]);
    translate([b-4, 155, 5]) cube([4, 46, 7.5]);
    string1 = str("right-front");
    translate ([10, 3, 4]) rotate([0, 0, 0])
    linear_extrude(2.0) text(string1, size = 6, direction = "ltr", spacing = 1 );
}

module right_back() {  //okay
    frame(y2+2*pd, z+2*pd, 5);
    string1 = str("right-back");
    translate ([10, 3, 4]) rotate([0, 0, 0])
    linear_extrude(2.0) text(string1, size = 6, direction = "ltr", spacing = 1 );
}

module left_back() {
    frame(y2+2*pd, z+2*pd, 5);
    //cable channel
    translate([y2-b, b-4, 5]) cube([4, z-2*b+4+4, 7.5]);
    //translate([b-4, b-4, 5]) cube([4, z-2*b+4+4, 7.5]);
    translate([b, z-b, 5]) cube([y2-2*b, 4, 7.5]);
    //translate([b-4, b-4, 5]) cube([y2-2*b+4, 4, 7.5]);
    string1 = str("left-back");
    translate ([10, 3, 4]) rotate([0, 0, 0])
    linear_extrude(2.0) text(string1, size = 6, direction = "ltr", spacing = 1 );
}

module back() {  
    difference() {
        union() {
        frame(x+2*pd, z+2*pd-20, 5);
        translate([0, 0, -2.5]) cube([x, z-20, 3]);
            //cable channel
    translate([b, b-4, 5]) cube([130, 4, 7.5-2]);
        }
        //cutout bottom
        translate([-10, -8, -4]) cube([240, 8, 10]);
        //cutout center
        translate([b, b, -4]) cube([(x+2*pd)-2*pd-2*b, (z+2*pd-20)-2*pd-2*b, 12]);
        //cutout camera tower holder
        translate([-10, 20+1, -4]) cube([250, 110, 10]);
        //cutout spindle
        translate([x-32.5, 5.1, -3]) cylinder(d=8.2, h=10);
        translate([x-32.5-8.2/2, -1, -3]) cube([8.2, 6.1, 10]);
        //cutout rack-holder
        translate([x-49.5, 9.3, 0]) cube([32, 4, 7.5]);
        //cutout motor cable
        translate([x-35-32, 3, -3]) cylinder(d=4, h=10);
        translate([x-35-32-4/2, -1, -3]) cube([4, 4, 10]); 
    //holes for screws
    h=z+2*pd-20;
    w=x+2*pd;
    n1=(h-2*pd)/2-6;  //h-2*pd = y1 or y2
    n2=(w-2*pd)/2-6;  //w-2*pd = x
    for (i=[0:2])
        translate([6, 6+i*n1, -4]) cylinder(d=2.8, h=12);
    for (i=[0:2])
        translate([w-2*pd-6, 6+i*n1, -4]) cylinder(d=2.8, h=12);
    for (i=[0:2])
        translate([6+i*n2, 6, -4]) cylinder(d=2.8, h=12); 
    for (i=[0:2])
        translate([6+i*n2, h-2*pd-6, -4]) cylinder(d=2.8, h=12);
    
    //additional holes for rF-box
    translate([58, 6, -4]) cylinder(d=2.8, h=12);
    translate([54, 184, -4]) cylinder(d=2.8, h=12);
    
    
    //cut in 2 parts: -10 to 100, 100 to 230
        //translate([100, -10, -5]) cube([130, 250, 20]);
    string1 = str("top-back");
    translate ([160, 185, 4]) rotate([0, 0, 0])
    linear_extrude(2.0) text(string1, size = 6, direction = "ltr", spacing = 1 );
    string2 = str("bottom-back");
    translate ([15, 3, 4]) rotate([0, 0, 0])
    linear_extrude(2.0) text(string2, size = 6, direction = "ltr", spacing = 1 );
        }
    //cable channel
    //translate([b, b-4, 5]) cube([130, 4, 7.5]);
     //test camera-holder
     //translate([0, 20, 0]) import("camera-holder-90Grad.stl");
     //translate([0, 95, 0]) cylinder(d=2.9, h=10);   
        w=x+2*pd;
    translate([-pd, 0, 0]) cube([pd+2, 6, 5]);
    translate([w-2*pd-2, 0, 0]) cube([pd+2, 6, 5]);
        //([w-2*pd-2, -pd, -1])
}

module top_front() {
    frame(x+2*pd, y1+2*pd, 5);
    //testing panel
    //translate([0, 0, 3]) import("panels_top-front.stl");
    string1 = str("top-front");
    translate ([20, 3, 4]) rotate([0, 0, 0])
    linear_extrude(2.0) text(string1, size = 6, direction = "ltr", spacing = 1 );
    difference() {
        translate([b, 89, 5]) cube([189, 7, 7]);
        //translate([b-1, 90, 5]) rotate([45, 0, 0]) cube([191, 11, 7]);
        translate([b-1, 90-1, 5]) rotate([45, 0, 0]) cube([191, 11, 7]);
    }
}

module top_back() {
    difference()  {
        frame(x+2*pd, y2+2*pd, 5);
        //srew hole top connector e-axis
        translate([215-5, y2-74.55, -1]) cylinder(d=3.9, h =10);
        string1 = str("top-back ↑");
    translate ([80, 140, 2]) rotate([0, 180, 0])
    linear_extrude(2.0) text(string1, size = 6, direction = "ltr", spacing = 1 );
        //cut for testing
        //translate([-10, -10, -2]) cube([200, 180, 10]);
    }
}
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

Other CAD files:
2LabsToGo-Eco-Hardware/3D-Parts/STL/x-axis/x-axis_cable_guide_top_left.stl
2LabsToGo-Eco-Hardware/3D-Parts/STL/electronic-box/electronic_box_frame-part1.stl
2LabsToGo-Eco-Hardware/3D-Parts/STL/humidity-control/humidity_control_drawer.stl
2LabsToGo-Eco-Hardware/3D-Parts/STL/humidity-control/humidity_control_drawer-handle.stl
2LabsToGo-Eco-Hardware/3D-Parts/openSCAD/x-axis/x-axis_cart-tensioner.scad
2LabsToGo-Eco-Hardware/3D-Parts/Autodesk Fusion/atomizer.f3d
2LabsToGo-Eco-Hardware/3D-Parts/Autodesk Fusion/electronic box.f3d
2LabsToGo-Eco-Hardware/3D-Parts/Autodesk Fusion/frames.f3d
2LabsToGo-Eco-Hardware/3D-Parts/Autodesk Fusion/plate holder.f3d
2LabsToGo-Eco-Hardware/3D-Parts/Autodesk Fusion/vialrack_v2.f3d
2LabsToGo-Eco-Hardware/3D-Parts/Autodesk Fusion/x-axis.f3d
2LabsToGo-Eco-Hardware/3D-Parts/Autodesk Fusion/y-axis.f3d
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

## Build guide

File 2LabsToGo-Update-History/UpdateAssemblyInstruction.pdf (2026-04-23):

Update Assembly Instruction

Software installation

With the operating system „Trixie“, opencv cannot be installed anymore with the pip command as described in the original Assembly Instruction.

Therefore, the opencv installation was included in install.py; thus, a manual installation is not required.
This opencv is only required for the Operational qualifications, while the software has its own opencv package.

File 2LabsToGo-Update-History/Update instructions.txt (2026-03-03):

Update instructions

1. Firmware update
Follow the instructions under 2LabsToGo-Eco-Firmware/ReadMe

2. Software update
The following instructions assume that the folder 2LabsToGo-Eco is located in the home directory.

2.1. Perform a back-up of the software folder!

2.2. Update procedure
* Disconnect the board (“Connection” tab in browser) and close all tabs.
* Stop the server with “Ctrl+c” in the running terminal.
* In the terminal, change to the 2LabsToGo-Eco directory
	cd ~/2LabsToGo-Eco
[The following commands require internet connection!]
* Then type
	git config pull.rebase false
  followed by
	git pull
=> All changes in the GitHub repository will be merged with the local Installation, but locally modified files will be maintained.

2.3 Start the software
* In the terminal, change to the software directory
	cd ~/2LabsToGo-Eco/2LabsToG-Eco-Software
  followed by 
    python3 run.py (or use the defined alias)

2.4 Open the browser and delete the cache to prevent loading old Java scripts.
* Open the browser’s menu and click on “Settings”.
* Search for “cache” and select ”Delete browsing data”.
* Select “All time” and “Cached images and files”.
* Click “Delete data”.

2.5 In a new browser tab, open the software (address: 127.0.0.1:8000).

3. Updates concern gcodegenerator.py and/or detections.js
If the update concerns the file GcodeGenerator.py, copy the data INIT_POINT_X and INIT_POINT_Y and the vial positions from the old software (back-up) to the updated software.
If the update concerns the file detection.js, copy the photo position from the old software (back-up) to the updated software.

3.1 INIT_POINT_X, INIT_POINT_Y points, and vial positions
To correct INIT_POINT_X and INIT_POINT_Y and the vial positions, open the file
	2LabsToGo-Software/app/finecontrol/gcode/GcodeGenerator.py
with Geany, overwrite the below exemplarily listed values by the values of the back-up file and save the file.

	INIT_POINT_X = 20
	INIT_POINT_Y = 3.5

	class GcodeGenerator:
		# set these values according to each machine!!!
		pos_common= "G0Z"
		vial_9= "145" #rinse bottle
		vial_8= "267.5" #vial 8
		vial_7= "253.5" #vial 7
		vial_6= "239.5" #vial 6
		vial_5= "225.5" #vial 5
		vial_4= "211.5" #vial 4
		vial_3= "197.5" #vial 3
		vial_2= "183.5" #vial 2
		vial_1= "169.5" #vial 1
		rin_bot= "145" #rinse bottle

3.2 Photo position 
To correct the photo position, open the file
	2LabsToGo-Software/app/templates/js/oclab/detection.js
with Geany and overwrite the Y value by the value of the back-up file and save the file.

	gcode = 'G1X90\nG28YZ\nG1Y158Z270F3000' //Y value depends on each system

4. In case of a complete new 2LabsToGo-Eco Installation (install.py and run.py have been executed), import the old database (methods and images) and the media folder (images, gcode files).
* Disconnect the board (“Connection” tab in browser) and close all tabs.
* Stop the server with “Ctrl+c” in the running terminal.
* Then execute in the terminal 
	cd app  (change to the directory 2LabsToGo-Eco/2LabsToGoEco-Software/app)
  followed by the next command
	python3 db-import.py
	
The Python script will rename the newly created and empty database db.sqlite3 to db-new.sqlite3	and rename the media folder to media-new.
Additionally, the Python script will delete all 0001_initial.py in migrations of sampleapp, finecontrol, development, and detection.

* From the backup, copy the old database (/app/db.sqlite3) and the media folder (/app/media) to the 2LabsToGo-Eco-Software/app folder of the new installation.

Executing python3 run.py will now perform the new migrations and load the old database.
	cd ..  (go back to the folder 2LabsToGo-Eco-Software)
	python3 run.py  (or type the created alias)

5. Special upgrade procedure if the database structure was modified
For this purpose, a Python script (update_db.py) will be available in the app folder, to be executed with 
	cd 2LabsToGo-Eco/2LabsToGo-Eco-Software/app
followed by
	python3 update_db.py
	
In Update history.txt, information concerning the changes are given.
The Python script will modify the database and also will delete all 0001_initial.py in migrations of sampleapp, finecontrol, development, and detection.

Executing python3 run.py will now perform the new migrations and load the modified database.
	cd ..  (go back to the folder 2LabsToGo-Eco-Software)
	python3 run.py  (or type the created alias)

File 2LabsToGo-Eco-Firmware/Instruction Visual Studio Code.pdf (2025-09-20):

Instruction Visual Studio Code

On the Raspberry Pi, start Visual Studio Code.
Therefore, click the raspberry (top left) and select Programming -> Visual Studio Code

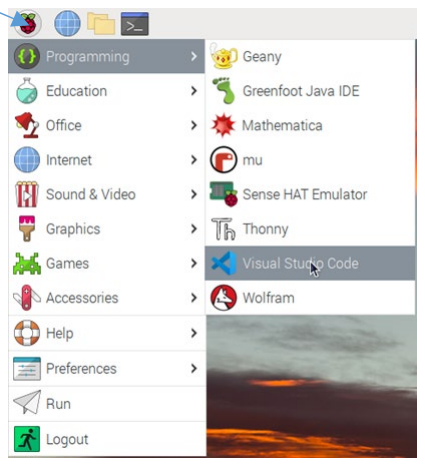
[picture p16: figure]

In Visual Studio Code, install Platformio IDE, if not already done. Click “Extensions”, search for platformio, and install Platformio IDE.

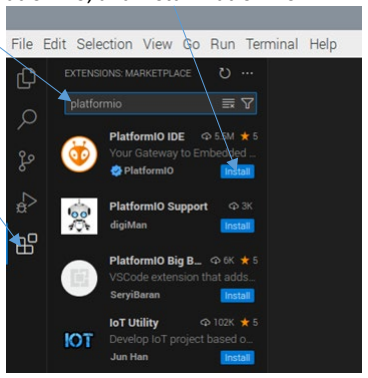
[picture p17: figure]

On the Welcome page, click Open Folder

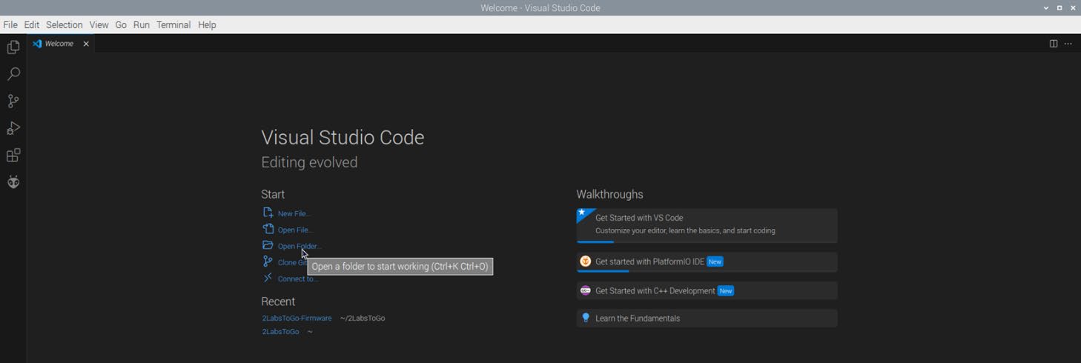
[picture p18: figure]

and select the folder .../2LabsToGo-Eco/2LabsToGo-Eco-Firmware/2LabsToGo-Eco-Marlin.

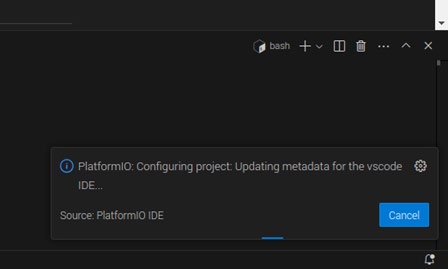
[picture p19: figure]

Wait for finishing the Platformio configuration (bottom right).

Click PlatformIO.

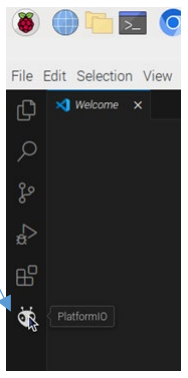
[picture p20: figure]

In the new menu PROJECT TASKS, expand “mega2560” and “General”, and click “Build”.

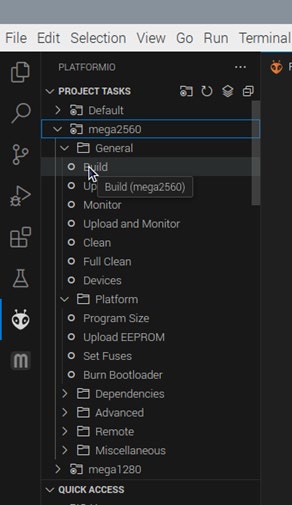
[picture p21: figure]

Building the firmware will start and will take some minutes. The progress can be followed in the terminal and should end with a “Success” message.

The firmware.hex file can be found in …/2LabsToGo-Eco/2LabsToGo-Eco-Firmware/2LabsToGo-Eco-Marlin/.pio/build/mega2560.

Open a new Linux Terminal and copy the firmware.hex file to the folder …/2LabsToGo-Eco/2LabsToGo-Eco-Firmware, while renaming it, for example, to my-firmware.hex:
cd ~/2LabsToGo-Eco/2LabsToGo-Eco-Firmware/2LabsToGo-Eco-Marlin
ls -a [to make the hidden files visible]
sudo cp .pio/build/mega2560/firmware.hex ~/2LabsToGo-Eco/2LabsToGo-Eco-Firmware/my-firmware.hex

Then open the file …/2LabsToGo-Eco-Firmware/flash_firmware.sh with Geany (right click) and correct the firmware filename:
#!/bin/bash

#read -p "Enter your username: " user

#echo "You entered $user"

#sudo avrdude -p atmega2560 -C avrdude_gpio.conf -c 2LabsToGo -v -U lfuse:w:0xff:m -U hfuse:w:0xd8:m -U efuse:w:0xfd:m

sudo avrdude -p atmega2560 -C avrdude_gpio.conf -c 2LabsToGo -v -U lfuse:w:0xff:m -U hfuse:w:0xd8:m -U efuse:w:0xfd:m
#sudo avrdude -p atmega2560 -C avrdude_gpio.conf -c 2LabsToGo -v -U flash:w:ArduinoISP.ino.hex:i

sudo avrdude -p atmega2560 -C avrdude_gpio.conf -c 2LabsToGo -v -U flash:w:ArduinoISP.ino.hex:i
#sudo avrdude -p atmega2560 -C avrdude_gpio.conf -c 2LabsToGo -v -U flash:w:firmware_2LabsToGo-Eco.hex:i sudo avrdude -p atmega2560 -C avrdude_gpio.conf -c 2LabsToGo -v -U flash:w:firmware_2LabsToGo-Eco.hex:i as to my-firmware. Keep the extension “.hex:i”(!) and save the file.

To flash the firmware, place the 4x2 jumper onto the ISP To Pi pins (center of the mainboard).
In the still open Linux Terminal (folder 2LabsToGo-Eco-Marlin), type
sudo chmod +x flash_firmware.sh [to make the file executable, if not done already before] and start flashing with
./flash_firmware.sh

The caselight will be switched off, and the flashing process will take some minutes, ending with the message “Thank you!”.

Remove the 4x2 jumper from the mainboard, when the firmware starts immediately (caselight on and homing the x-axis).

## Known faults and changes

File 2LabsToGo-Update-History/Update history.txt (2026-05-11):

Update history

Date: 05-10-2025
Done: General software update
Concerned: many files

Date: 06-03-2025
Done: Update for humidity-control
Concerned: 
2LabsToGo-Eco-Hardware/3D-parts (openSCAD, STL), 
2LabsToGo-Eco-Hardware/Materials-Lists (Bill of Materials_humidity-control, additional baskets),
2LabsToGo-Eco-Firmware (Marlin, firmware hex file)

Date: 07-25-2025
Done: Sample tables updated (application pattern changes without erasing the sample table)
Concerned:
2LabsToGo-Eco-Software/app/templates/js/oclab/sample.js
2LabsToGo-Eco-Software/app/templates/js/oclab/samplesp.js
2LabsToGo-Eco-Software/app/templates/modules/loadlist/loadlist.js
2LabsToGo-Eco-Software/app/templates/modules/sampleapp/table/table.js
2LabsToGo-Eco-Software/app/templates/modules/sampleappsp/tablesp/tablesp.js

Date: 08-22-2025
Done: Method Finecontrol/Dispensing valve corrected
Concerned:
2LabsToGo-Eco-Software/app/templates/modules/dispensevalve/dispensevalve.js

Date: 09-08-2025
Done: Electronic box modified for humidity Control; two-parted frame added to support the old model
Concerned:
2LabsToGo-Eco-Hardware/3D-Parts/Autodesk Fusion/electronic box.3fd
2LabsToGo-Eco-Hardware/3D-Parts/STL/electronic-box/electronic_box.stl
2LabsToGo-Eco-Hardware/3D-Parts/STL/electronic-box/electronic_box_frame-part1.stl
2LabsToGo-Eco-Hardware/3D-Parts/STL/electronic-box/electronic_box_frame-part2.stl

Date: 09-20-2025
Done: README in main updated
Done: Instruction Visual Studio Code corrected

Date: 09-22-205
Done: Humidity Control updated (Firmware and Software), now allowing both drying and humidifying the 2LabsToGo-Eco before development.
Concerned:
2LabsToGo-Eco-Firmware (Marlin; firmware_2LabsToGo-Eco.hex)
2LabsToGo-Eco-Software/app/templates/modules/humiditycontrol/humiditycontrol.html
2LabsToGo-Eco-Software/app/templates/modules/humiditycontrol/humiditycontrol.js

Date: 10-13-2025
Done: README in main updated
Concerned: Raspberry Pi operating system "bullseye" 

Date: 11-18-2025
Done: Some files have been cleaned up.
Concerned: migrations, update is not required

Date: 12-02-2025
Done:  Java scripts updated, now better working
Concerned: drypump.js, dispensvalve.js, wayvalve.js

Date: 03-03-2026
Done: Updates to Django 5, Debian 13 (Trixie), and Raspberry Pi 5B
Concerned: Many files, but not GcodeGenerator.py and detection.js

Date: 03-03-2026
Done: 3D files atomizer optimized
Concerned: atomizer.f3d (Fusion file), nebulizer_atomizer_part-1.stl, nebulizer_atomizer_part-2.stl, nebulizer_atomizer_washer.stl

Date: 04-03-2026
Done: Operational qualification updated
Concerned: Different folders Operational_qualificaction added (Pi4-bullseye, P4-trixie, P5-trixie)

Date: 04-05-2026
Done: Electronics updated
Concerned: 2LabsToGo-Eco-Hardware/Electronics

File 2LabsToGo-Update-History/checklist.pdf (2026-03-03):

### checklist

Before installing the software, please note the following points.

Git clone, updates and installation of software packages require internet access!

- Static IP address for LAN connection was entered in the Raspberry Pi (ask your IT service how to apply for an IP address).

[Alternatively, wireless LAN was configured: Connect Raspberry Pi to WiFi: Step-by-Step Guide.] (https://linuxconfig.org/connecting-your-raspberry-pi-to-wi-fi-a-how-to)

- Firmware was successfully flashed.

Then open a Linux terminal

and execute the follwing commands:

cd /home/to-my-folder/2LabsToGo-Eco/2LabsToGo-Eco-Software

sudo python3 install.py |& tee install-py.txt

This will update and upgrade the operating system, follwed by the installation of software packages. All procedures are logged in install-py.txt.

sudo python3 run.py |& tee run-py.txt

- The first run.py takes a while!

This will install the docker image and create the docker containers, perform the Django migrations and connect to the Django server.
With the terminal message “Quit the server with CONTROL-C.”, the software is ready to go.
- Open a browser and enter “127.0.0.1:8000” in the address field.

The connection tab will be opened followed by opening the user management.

- Register a new user.

Thereafter, the software is ready to be used.

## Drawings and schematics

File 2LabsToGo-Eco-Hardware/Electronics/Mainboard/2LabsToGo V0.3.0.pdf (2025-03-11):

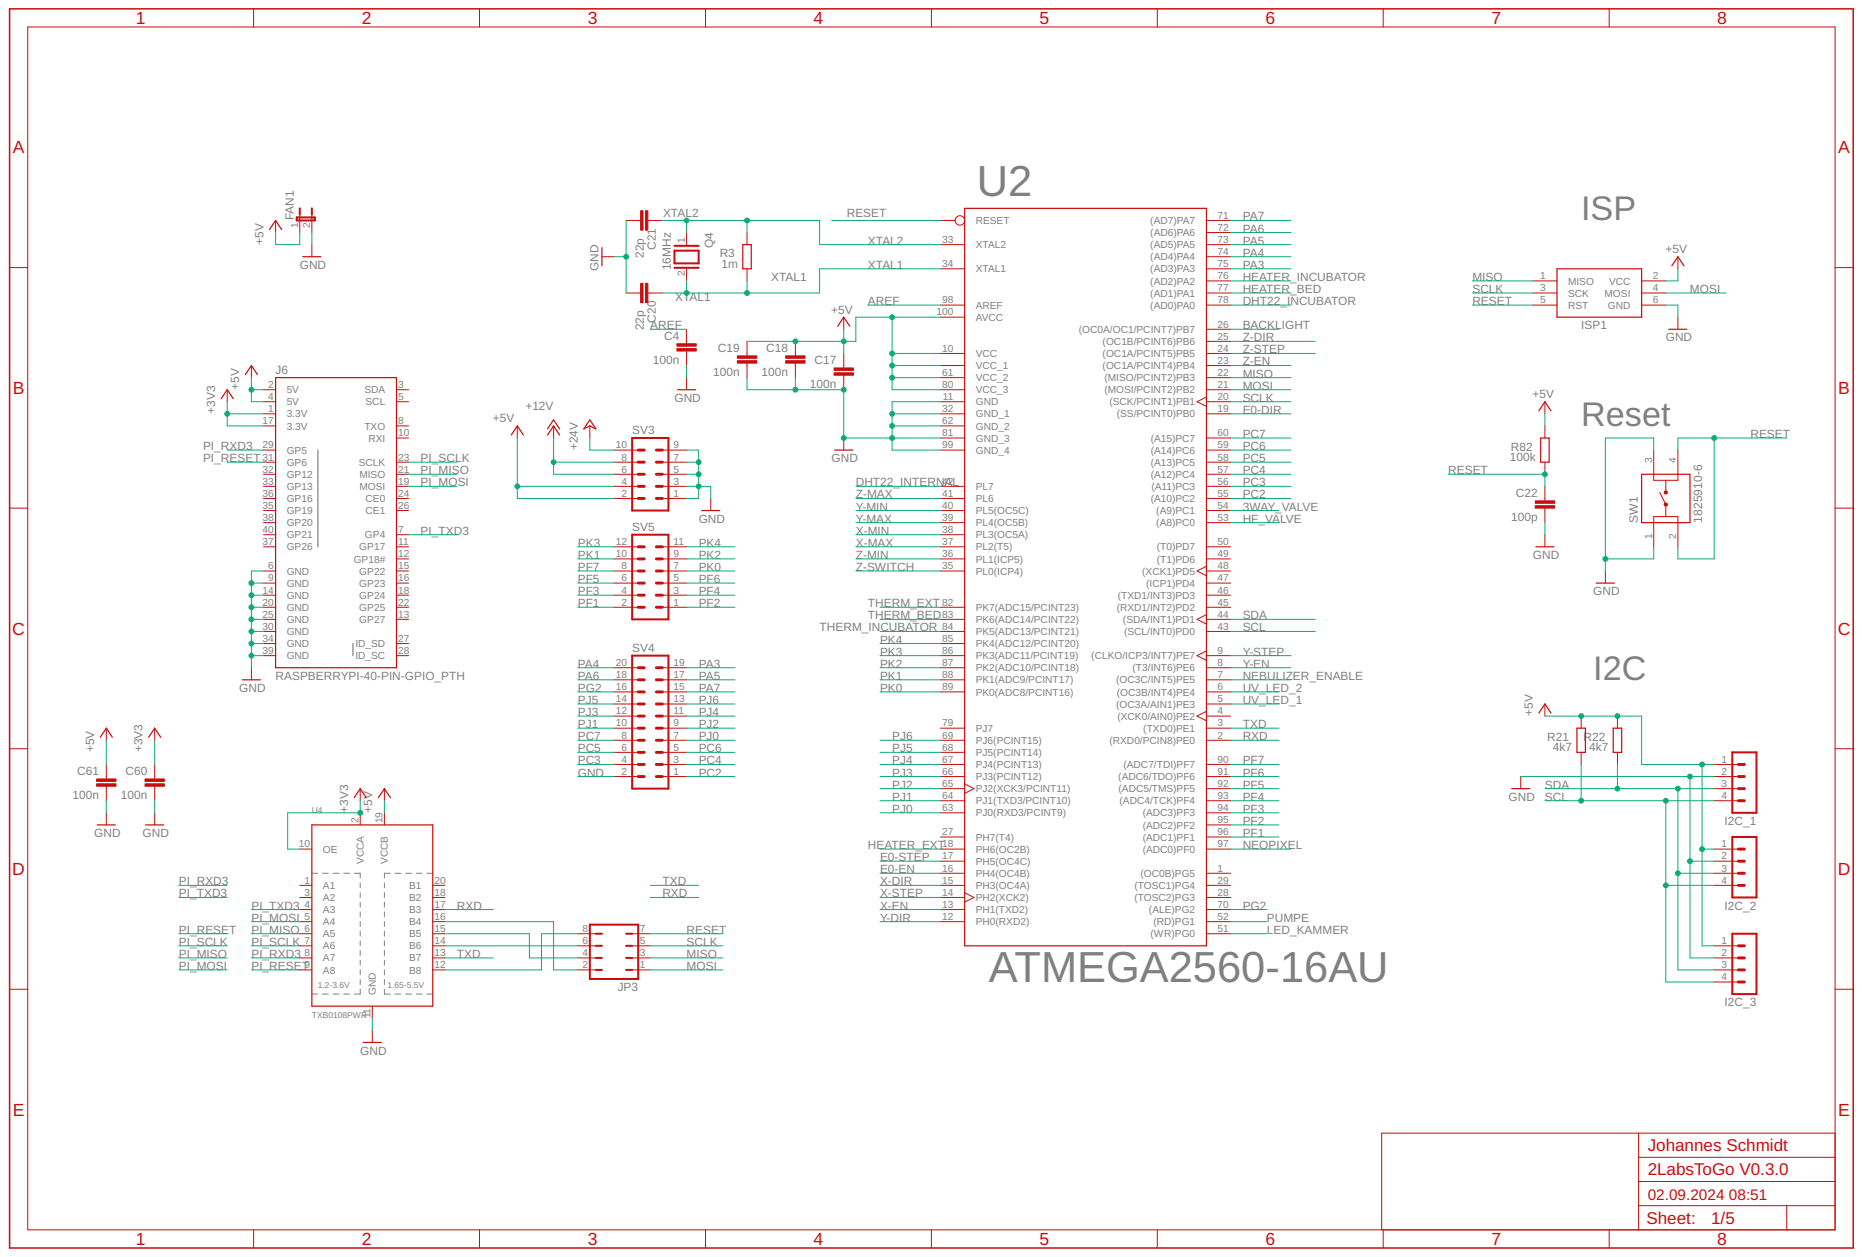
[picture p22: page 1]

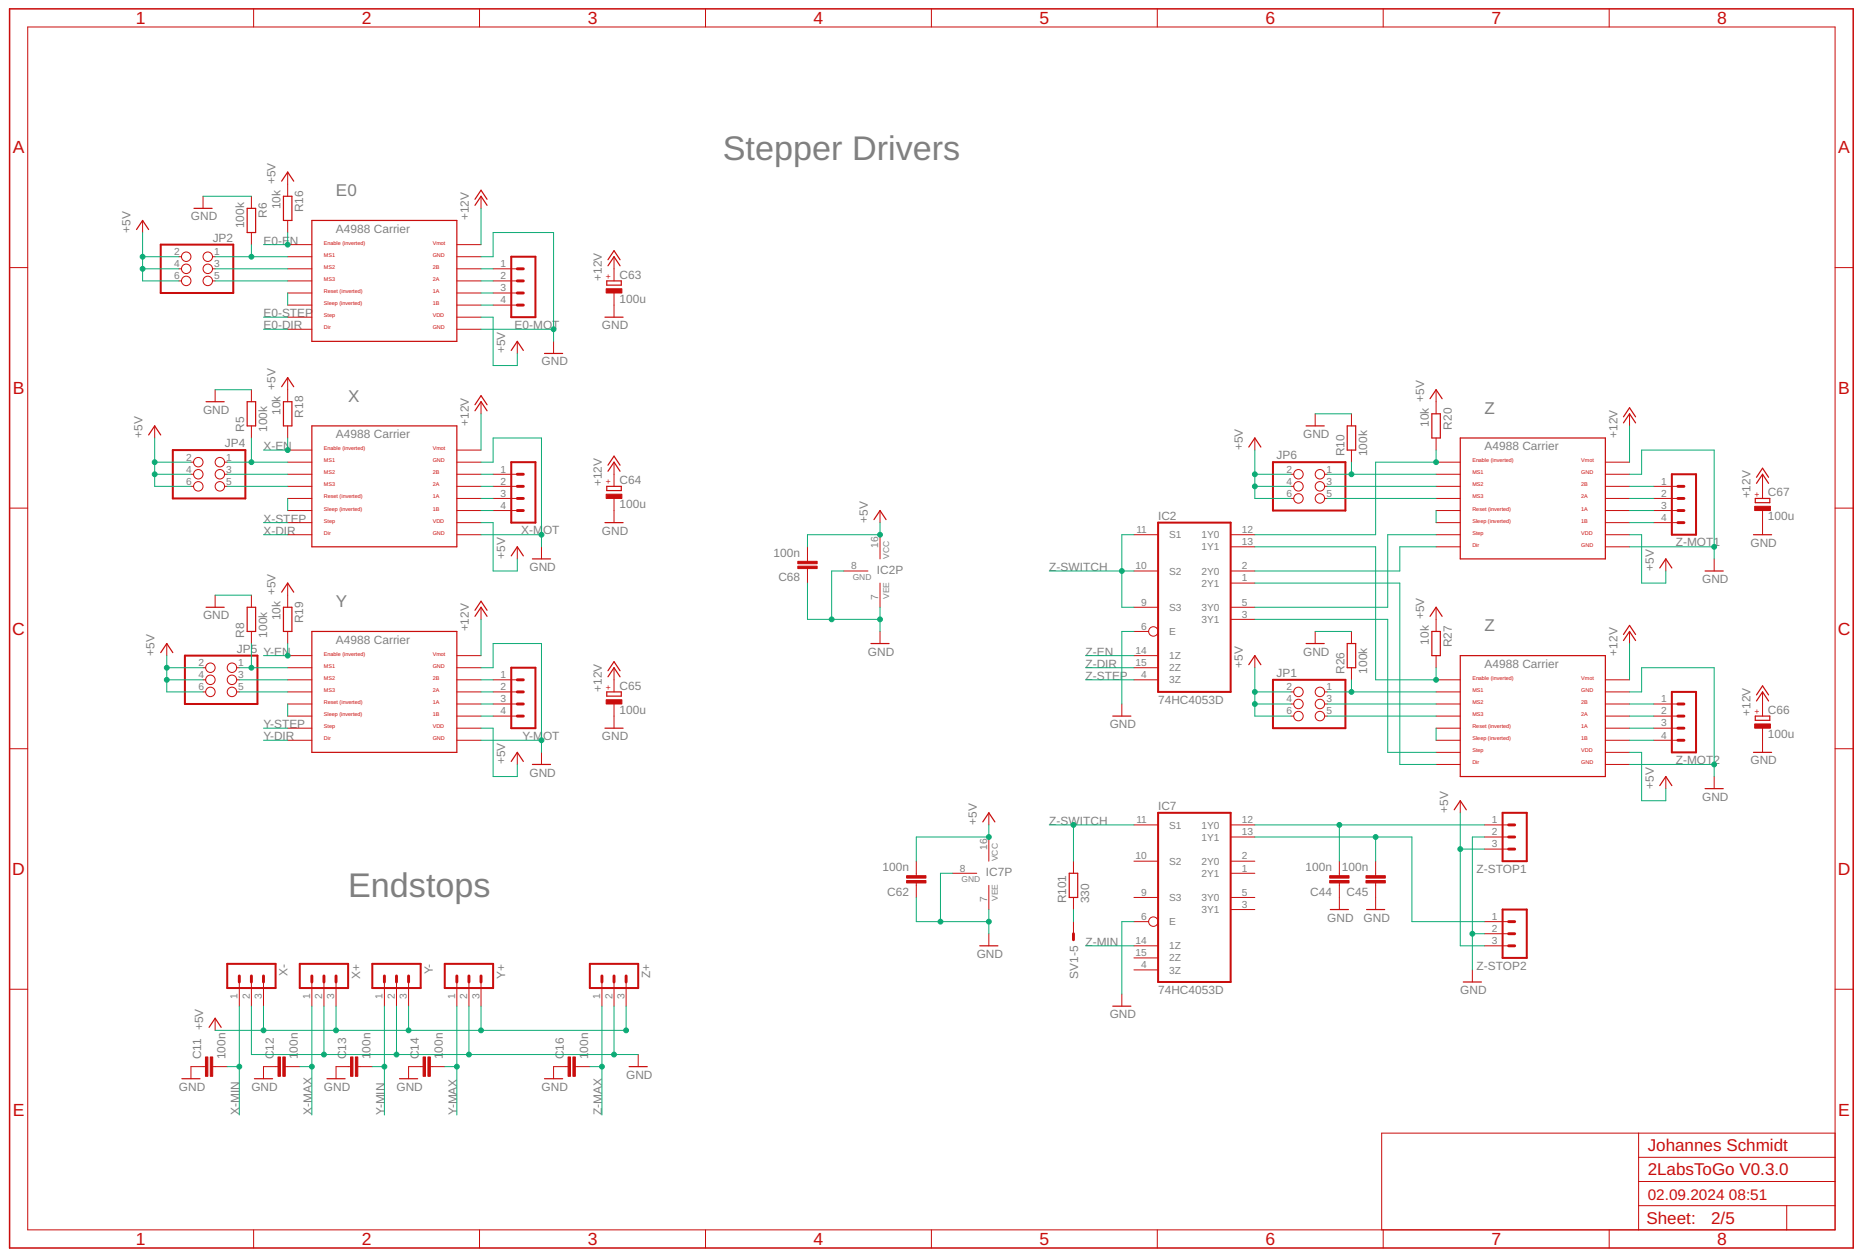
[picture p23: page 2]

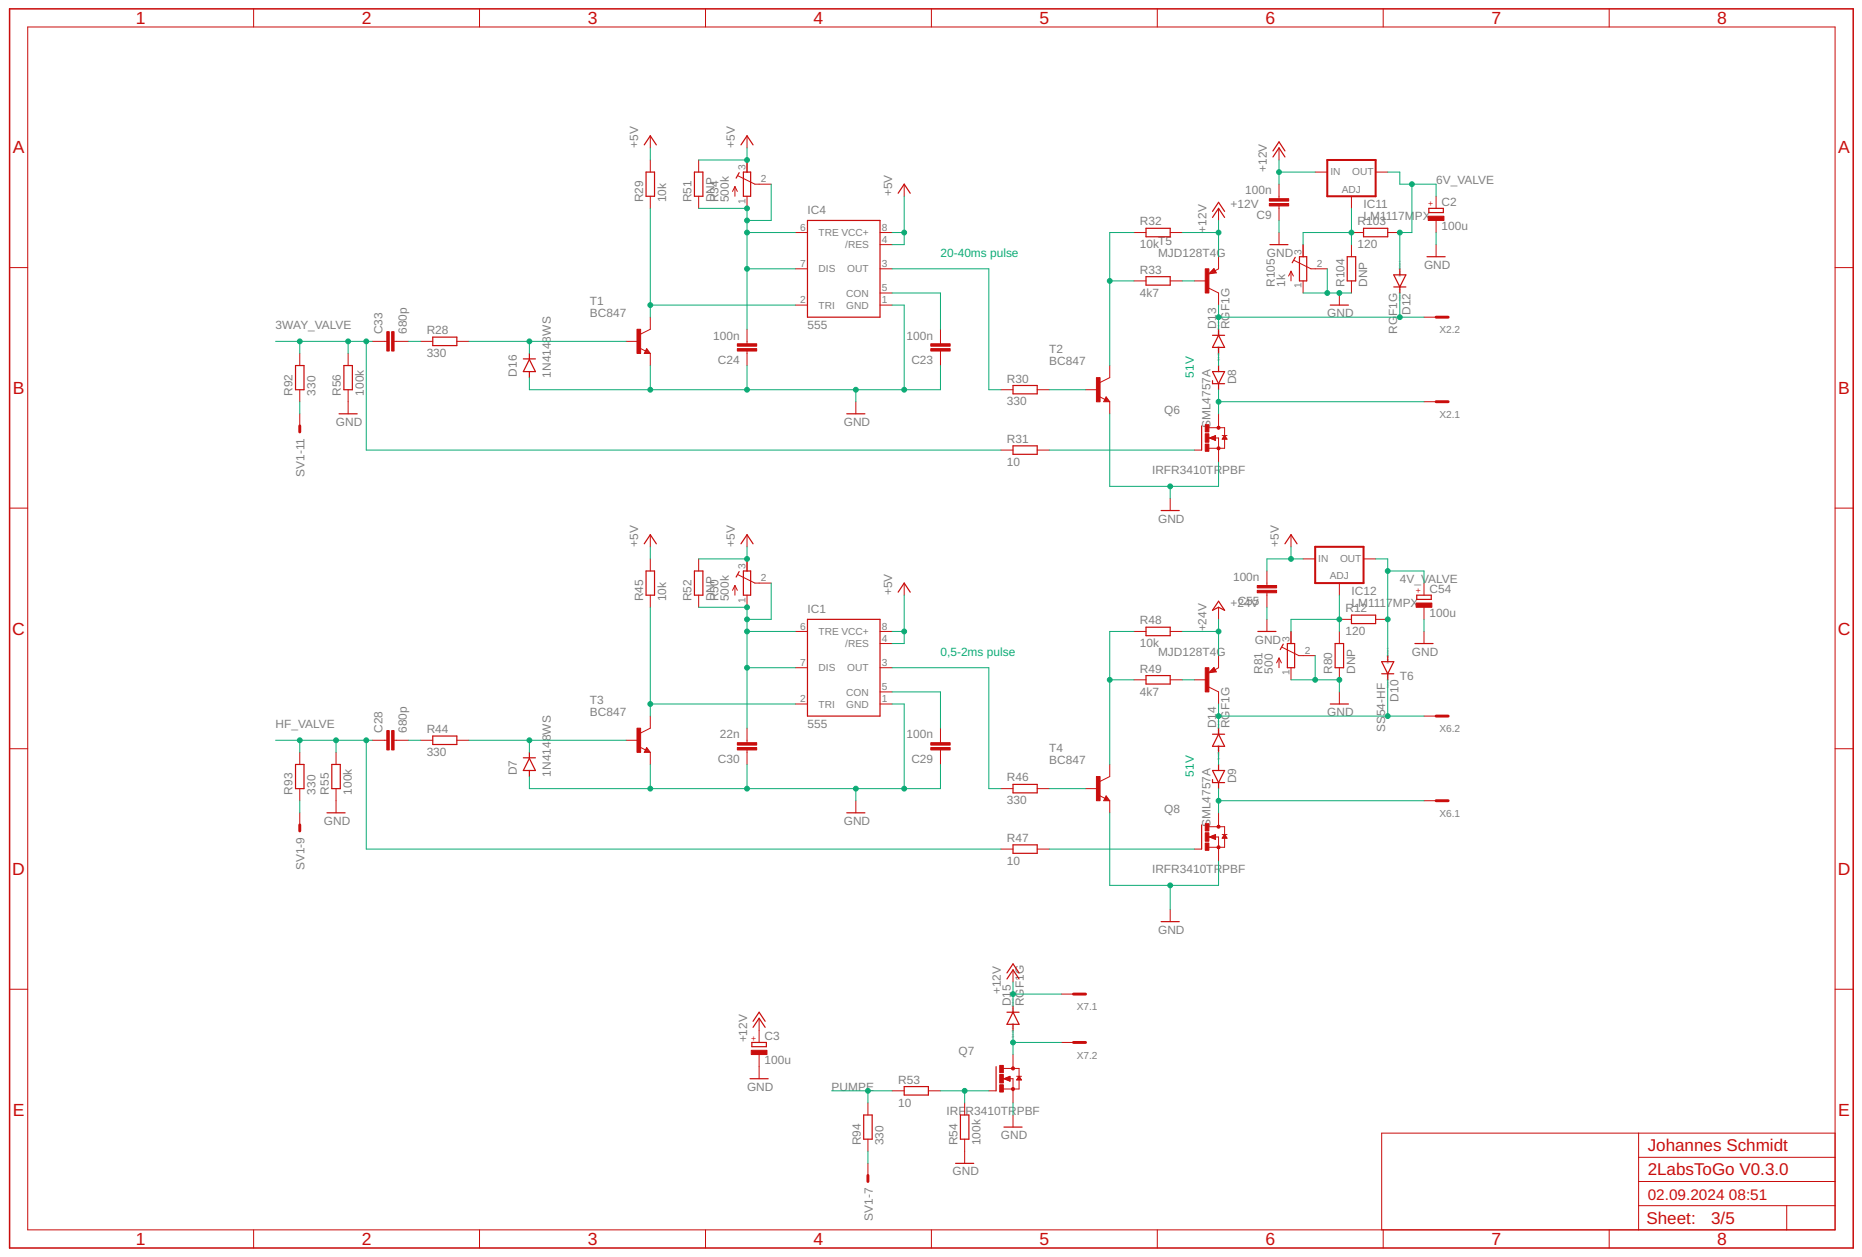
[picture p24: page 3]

SpiceOrder 1 SpiceOrder 2 SpiceOrder 1 SpiceOrder 2 SpiceOrder 1 SpiceOrder 2 SpiceOrder 1 SpiceOrder 2 SpiceOrder 1 SpiceOrder 2 330 10k 330 10 10k 4k7 680p 100n 100n GND GND 500k +5V +5V +5V IRFR3410TRPBF BC847 BC847 555 +12V 330 10k 330 10 10k 4k7 680p 22n 100n GND GND 500k +5V +5V +5V IRFR3410TRPBF BC847 BC847 555 +24V MJD128T4G MJD128T4G DNP DNP IRFR3410TRPBF 10 100k 100k 100k GND GND GND GND +12V +5V 120DNP 500 GND SML4757A SML4757A SS54-HF RGF1G RGF1G RGF1G RGF1G 330 330 330 +12V GND100u 100u GND 100nGND 1N4148WS 1N4148WS 120DNP 1k 100u GND 100nGND GND +12V LM1117MPX LM1117MPX R28 R29 R30 R31 R32 R33 C33 C24 C23 1 3 2 R34 Q6 T1 T2 TRE 6 OUT 3 DIS 7 TRI 2 VCC+ 8 GND 1 CON 5 /RES 4 IC4 R44 R45 R46 R47 R48 R49 C28 C30 C29 1 3 2 R50 Q8 T3 T4 TRE 6 OUT 3 DIS 7 TRI 2 VCC+ 8 GND 1 CON 5 /RES 4 IC1 T5 T6 R51 R52 Q7 R53 R54 R55 R56 R12 R80 1 3 2 R81 D8 D9 D10 D12 D13 D14 D15 R92 R93 R94 C3 SV1-11 X2.1 X2.2 X6.1 X6.2 X7.1 X7.2 C54 C55 D7 D16 SV1-9 SV1-7 R103 R104 1 3 2 R105 C2 C9 ADJ IN OUTIC11 ADJ IN OUTIC12 +12V 3WAY_VALVE +24V PUMPE 4V_VALVE HF_VALVE 6V_VALVE Johannes Schmidt Sheet: ABCDE 1 2 3 4 5 6 7 8 ABCDE 1 2 3 4 5 6 7 8 2LabsToGo V0.3.0 02.09.2024 08:51 3/5 + + + 0,5-2ms pulse 20-40ms pulse 51V 51V

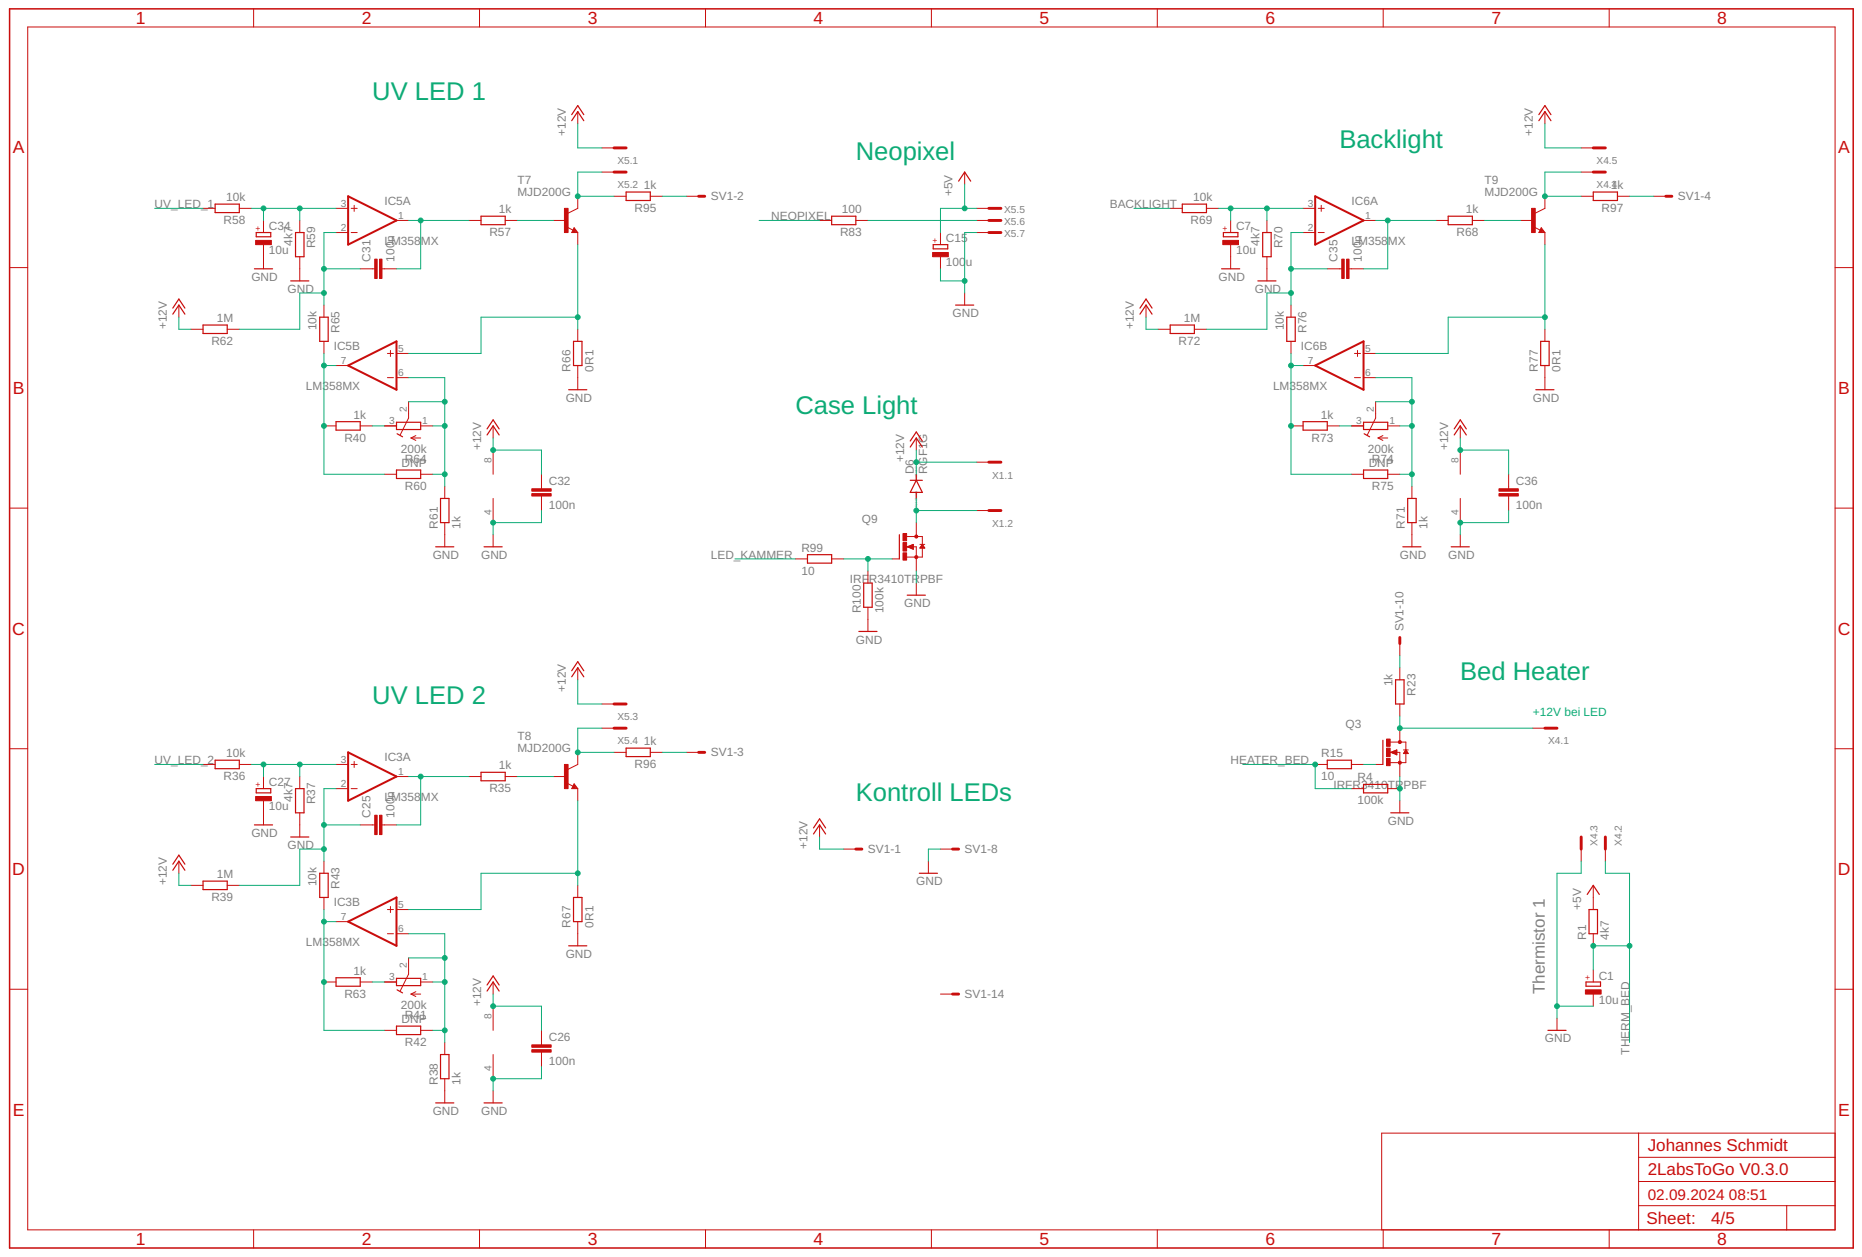
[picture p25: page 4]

SpiceOrder 1 SpiceOrder 2 LM358MX LM358MX 100n 100n 1k 10k 4k7 1k 1M GND 200k DNP 10k +12V 10uGND GND GND +12V 0R1 MJD200GGND +12V LM358MX LM358MX 100n 100n 1k 10k 4k7 1k 1M GND 200k DNP 10k +12V 10uGND GND GND +12V 0R1 MJD200GGND +12V LM358MX LM358MX 100n 100n 1k 10k 4k7 1k 1M GND 200k DNP 10k +12V GND GND GND +12V 0R1 MJD200GGND +12V 100 GND +5V 100u 1k1k 1k IRFR3410TRPBF 10 100k GND GND +12V RGF1G +12V GND GND 100k 10 1k 4k7 GND 10u 10u IRFR3410TRPBF +5V 1k1k 1k 23 1 IC5A65 7 IC5B C31 C32 R57 R58 R59 R61 R62 3 1 2 R64 R60 R65 C34 8 4 R66 T7 23 1 IC3A65 7 IC3B C25 C26 R35 R36 R37 R38 R39 3 1 2 R41 R42 R43 C27 8 4 R67 T8 23 1 IC6A65 7 IC6B C35 C36 R68 R69 R70 R71 R72 3 1 2 R74 R75 R76 8 4 R77 T9 R83 C15 R95 R96 R97 Q9 R99 R100 D6 SV1-1 SV1-2 SV1-3 SV1-4 SV1-8 SV1-14 R4 R15 R23 R1 C1 X5.1 X5.2 X5.3 X5.4 X5.5 X5.6 X5.7 X1.1 X1.2 X4.1 X4.2 X4.3 X4.4 X4.5 C7 Q3 SV1-10 R40 R63 R73 UV_LED_1 UV_LED_2 NEOPIXEL LED_KAMMER HEATER_BED THERM_BED BACKLIGHT Johannes Schmidt + + Sheet: ABCDE 1 2 3 4 5 6 7 8 ABCDE 1 2 3 4 5 6 7 8 2LabsToGo V0.3.0 02.09.2024 08:51 4/5 + + + UV LED 1 UV LED 2 Backlight Neopixel Case Light Kontroll LEDs +12V bei LED Bed Heater Thermistor 1

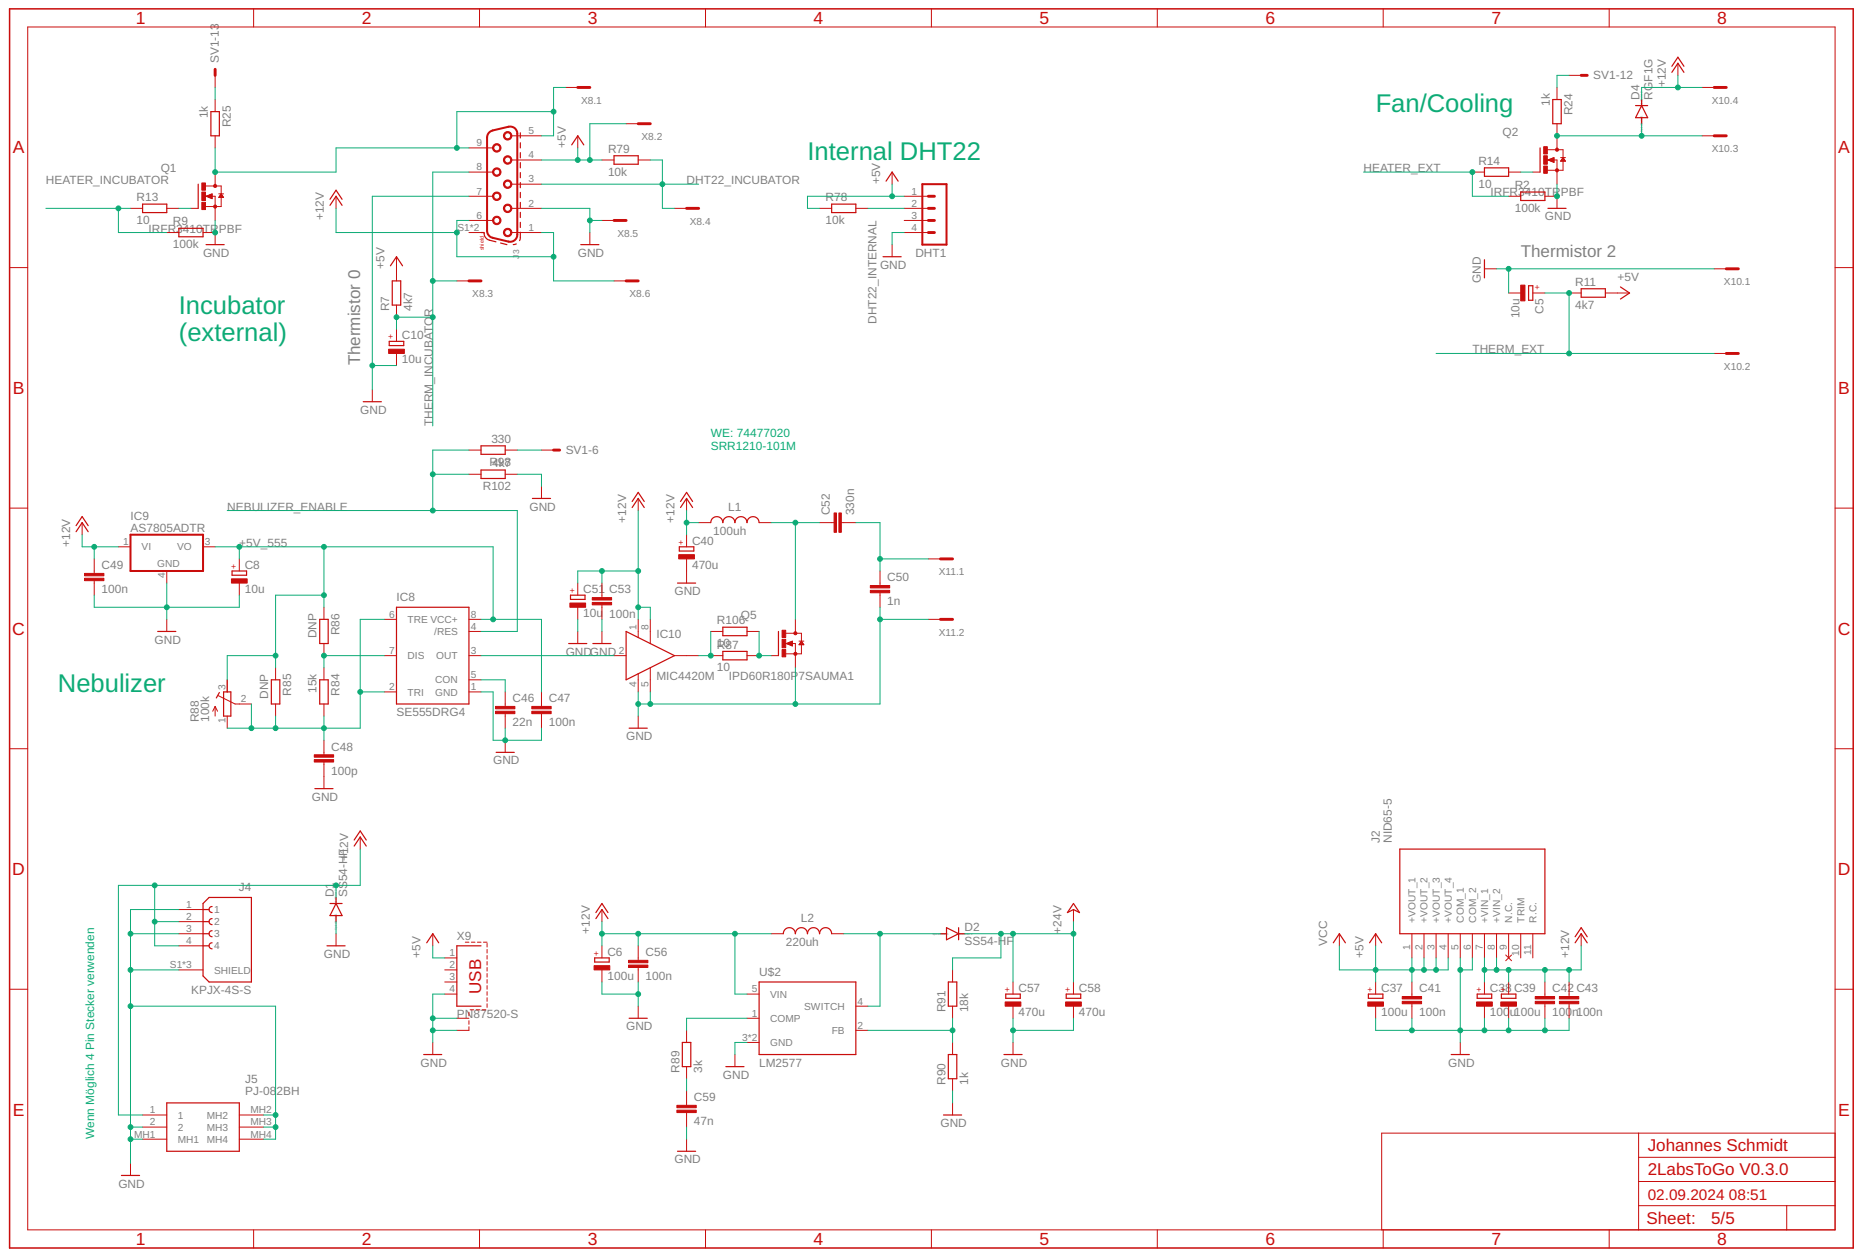
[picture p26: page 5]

Wenn Möglich 4 Pin Stecker verwenden

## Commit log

2025-05-10 Software updated 05102025
    [autosampler_vialrack_ver2.stl, vialrack_v2.f3d, vialrack_ver2.scad]
2025-05-15 Dold basket added
    [Dold-basket.xlsx]
2025-06-03 updated 06032025
    [Amazon-basket.xlsx, Bill of Materials_2LabsToGo-Eco.xlsx, Bill of Materials_humidity-control.xlsx, DigiKey-basket.xlsx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]
2025-06-13 electronics updated
    [Digikey-mainboard_SMD-parts.xlsx, Digikey-mainboard_through-hole-parts.xlsx, Mouser-mainboard_SMD-parts_no-ATMega.xlsx, Mouser-mainboard_through-hole-parts.xls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]
2025-07-15 sample table updated, 15.07.2025
2025-07-25 sample tables updated 07252025
2025-09-08 electronic box updated
    [electronic box.f3d, electronic-box.stl, electronic_box.stl, electronic_box_frame-part1.stl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]
2025-11-05 stl file added
    [multifunctional_plate_holder-cover_development_glass-plate_cover.stl]
2026-03-03 3D files atomizer revised
    [atomizer.f3d, nebulizer_atomizer_part-1.stl, nebulizer_atomizer_part-2.stl, nebulizer_atomizer_washer.stl]
2026-04-05 back_humidity-control.dxf added
    [back_humidity-control.dxf]
2026-04-05 frame_back modified for humidity control
    [frames.f3d]
